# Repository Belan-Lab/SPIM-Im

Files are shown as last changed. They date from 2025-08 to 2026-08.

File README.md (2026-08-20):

Stand With Ukraine (https://stand-with-ukraine.pp.ua)

Selective Plane Illumination Microscopy Setup
==================================

_Fluorescence Imaging Laboratory, Kyiv, Ukraine_

<p align="center">
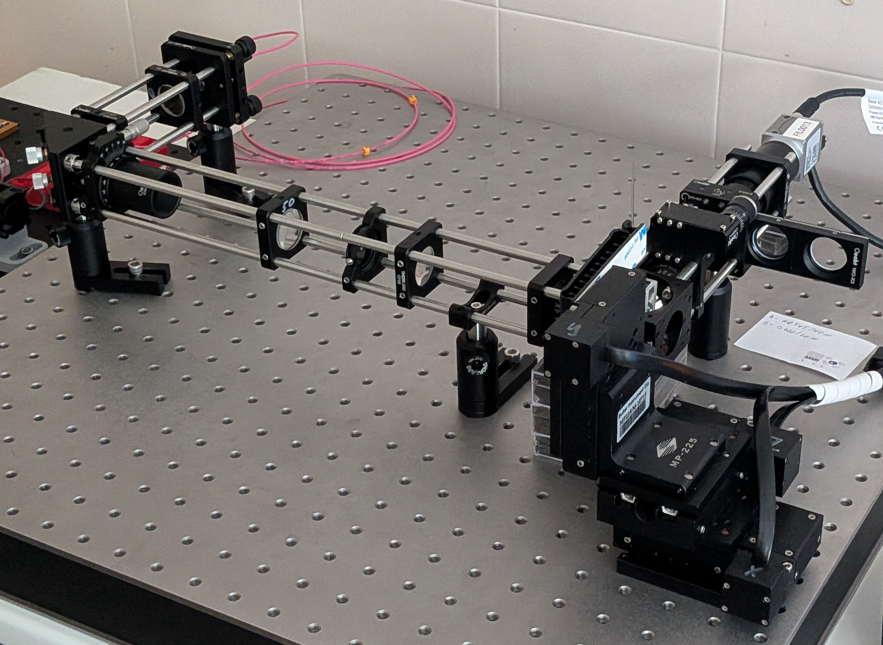
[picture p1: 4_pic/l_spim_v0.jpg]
</a>
</p>
__L-SPIM v0__

# L-SPIM v0 parameters overview

| Parameter                                      | Value                                                        |
| ---------------------------------------------- | ------------------------------------------------------------ |
| Detection objective                            | Olympus PlaN 10x 0.25                                        |
| Magnification                                  | 5.56x                                                        |
| Camera                                         | Basler Ace 2R Pro (a2A5320-23umPRO), 5320x3032 px (16.1 Mpx) |
| Pixel size                                     | 0.493 μm/px                                                  |
| Field of view                                  | 2.62x1.49 mm                                                 |
| Z-stack step resolution                        | 16 μstep/μm (0.0625 μm/μstep)                                |
| Lateral resolution, FWHM theoretical/estimated | 1.12 μm/2.06 μm                                              |
| Axial resolution, FWHM theoretical/estimated   | 11.70 μm/ 6.32 μm                                            |
| Excitation lasers                              | 510 nm, 640 nm                                               |
| Emission filters                               | Chroma HQ545/40m, Chroma D620/20m                            |

# Detection arm

## Detection params
| Parameter                                              | Value                               |
| ------------------------------------------------------ | ----------------------------------- |
| Detection objective                                    | Olympus PlaN 10x 0.25 FN 22 (F18)   |
| Detection tube lens                                    | F100                                |
| Magnification                                          | ~5.56x                              |
| Camera                                                 | Basler Ace 2R Pro (a2A5320-23umPRO) |
| Pixel size                                             | 0.493 μm/px                         |
| Field of view                                          | 2.62x1.49 mm                        |
| Theoretical resolution (500 nm)                        | 1.220 μm                            |
| Theoretical depth of field (500 nm, n=1.33)            | 10.640 μm                           |
| Z-stack step (Sutter Instruments MPC-200 with MP225/M) | 0.0625 μm/μstep (16 μstep/μm)       |

## Filters

# Excitation arm
## Light path

## Lasers

# Control software
## Micromanager configuration

## Camera
| Model           | Basler Ace 2R        |
| --------------- | -------------------- |
| ID              | a2A5320-23umPRO      |
| Sensor          | Sony IMX542 (CMOS)   |
| Sensor size     | 14.58x8.31 mm (1.1") |
| Sensor diagonal | 16.78 mm             |
| Pixels (HxV)    | 5320x3032 (16.1 Mpx) |
| Pixel size      | 2.74x2.74 μm         |
| Frame rate      | up to 24 fps         |

### GPIO pinout

|Pin|Function|I/O Line|Colour|
|-|-|-|-|
|1|12–24 VDC camera power|-|Brown|
|2|Opto-coupled I/O input line|Line 1|White|
|3|Ground for opto-coupled I/O line|-|Blue|
|4|General purpose I/O (GPIO) line|__Line 2__|Black|
|5|General purpose I/O (GPIO) line|Line 3|Grey|
|6|Ground for camera power and General Purpose I/O (GPIO) lines|-|Pink|

[Basler Power-I/O Cable](https://docs.baslerweb.com/basler-power-io-cable-m8-6p-open-p)

### GPIO configuration
Pylon Viewer v7.2 camera parameters, category __Digital I/O Control__:

- __Line Selector:__ Line 2
- __Line Inverter:__ not selected
- __Line Mode:__ Output
- __Line Source:__ Acquisition Active

<p align="center">
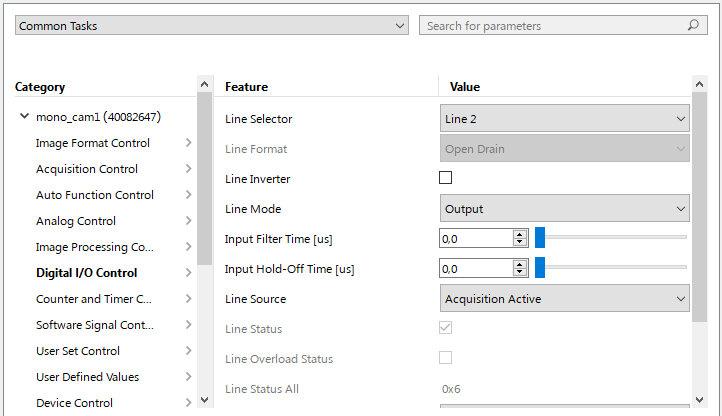
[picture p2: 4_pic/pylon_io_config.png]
</a>
</p>

## Sync

Synchronisation with [Arduino32bitBoards](https://micro-manager.org/Arduino32bitBoards), specs for ESP32:

- Baudrate: 115200
- Laser TTL trigger module requires 5V, need level conversion 3.3V -> 5V

__Pinout:__
- Trigger: __Pin 5 - camera Line 2 input__
- Channel 1: __Pin 25/DAC - Level Converter ON__
- Channel 2: __Pin 26/DAC - 510 nm trigger__
- Channel 3: __Pin 27/PWM - 640 nm trigger__
- Channel 4: Pin 15/PWM
- Channel 5: Pin 14/PWM
- Channel 6: Pin 4/PWM
- Channel 7: Pin 23/PWM
- Channel 8: Pin 19/PWM

__Switch states__
|Laser|Pin Hight|State|
|-|-|-|
|510 nm|25+26 (Ch.1+Ch.2)|3|
|640 nm|25+27 (Ch.1+Ch.3)|4 (not working)|
|510 nm + 640 nm|25+26+27 (Ch.1+Ch.2+Ch.3)|6 (not working)|

## Hardware config

# License 
This open-source project is released under the CERN Open Hardware License. Our aims are to promote open scientific hardware development and to share our engineering solutions.

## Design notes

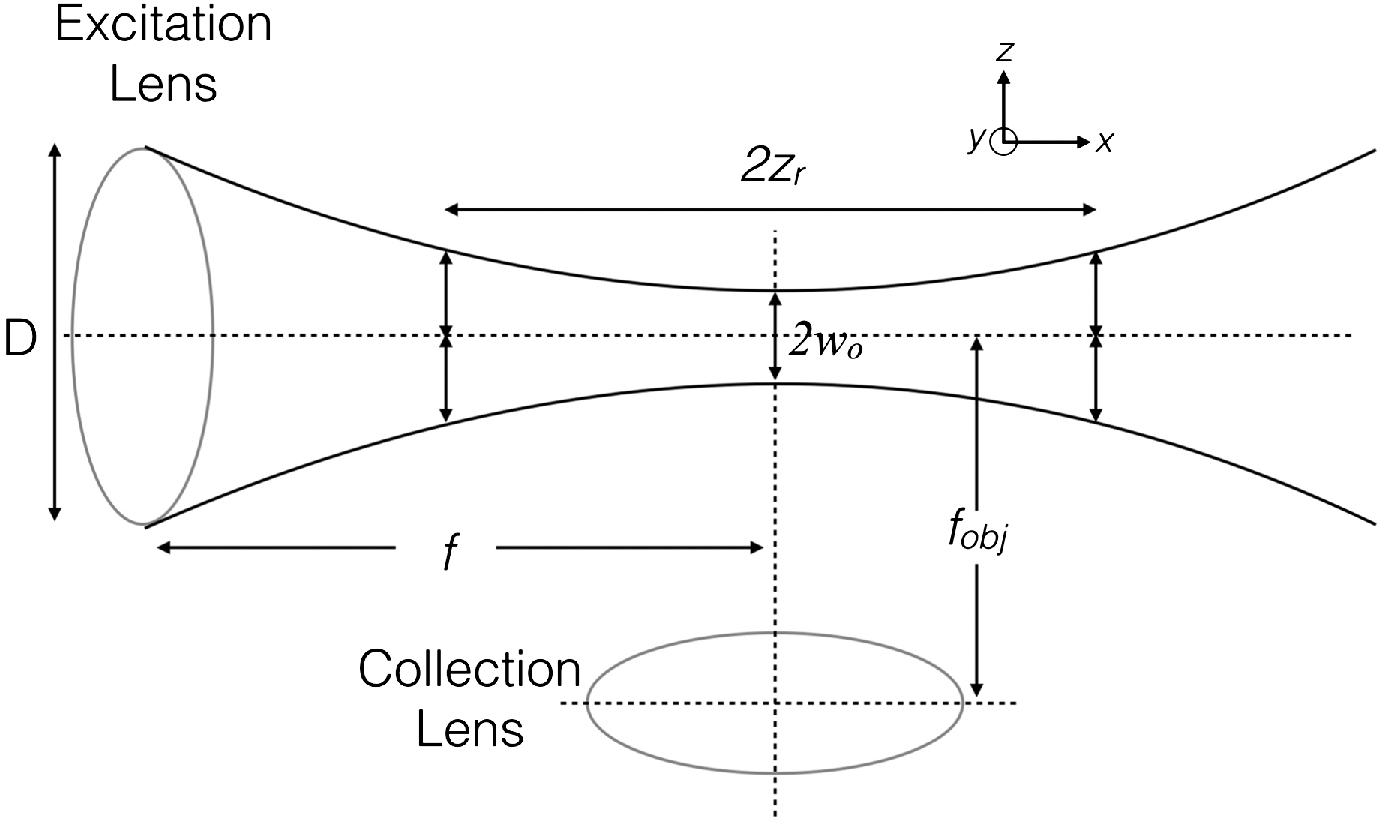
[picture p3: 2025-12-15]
3_notes/pic/ls_geom_olarte2017.jpeg

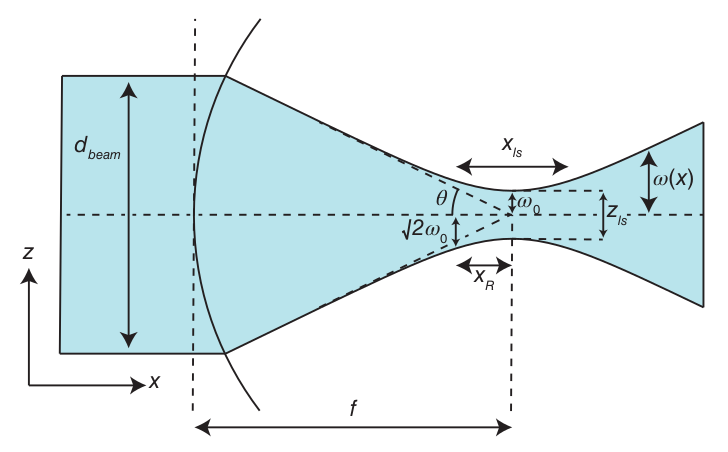
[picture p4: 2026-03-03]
3_notes/pic/gaussian_beam.png

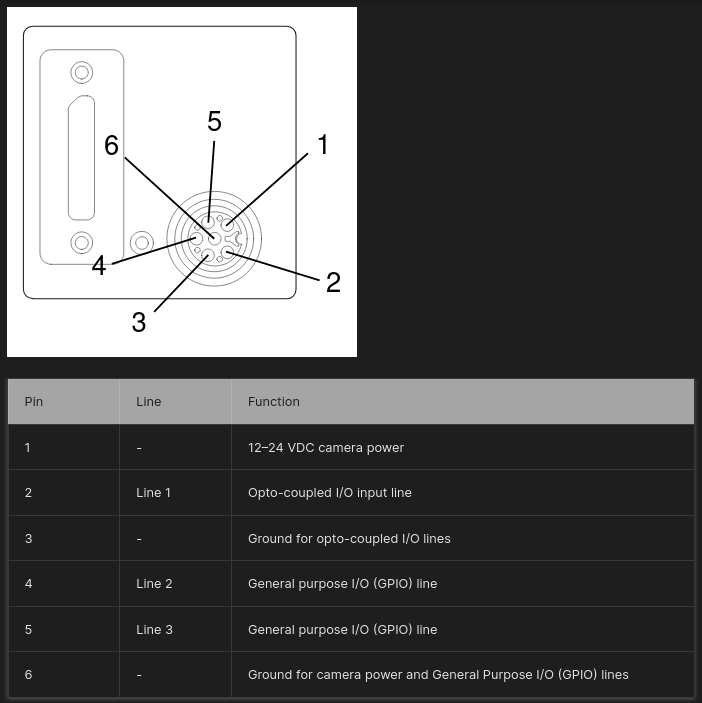
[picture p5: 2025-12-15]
3_notes/pic/GPIO_Ace2R.png

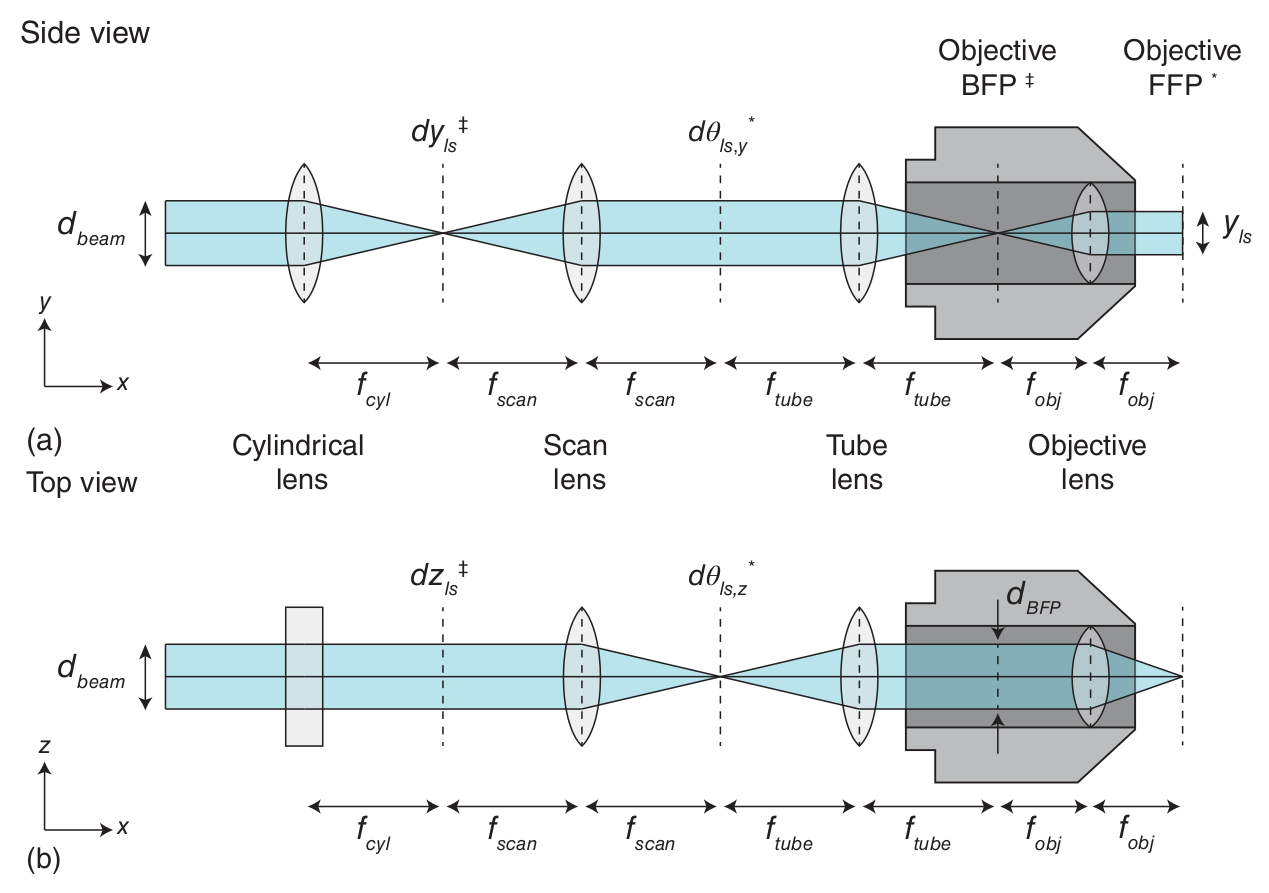
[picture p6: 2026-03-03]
3_notes/pic/illumination_path.png

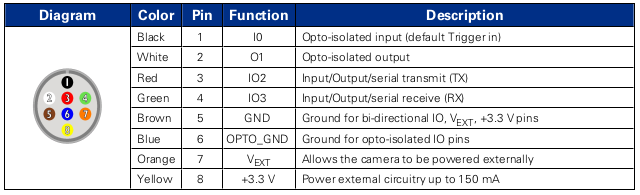
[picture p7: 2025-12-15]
3_notes/pic/GPIO_GS3.png

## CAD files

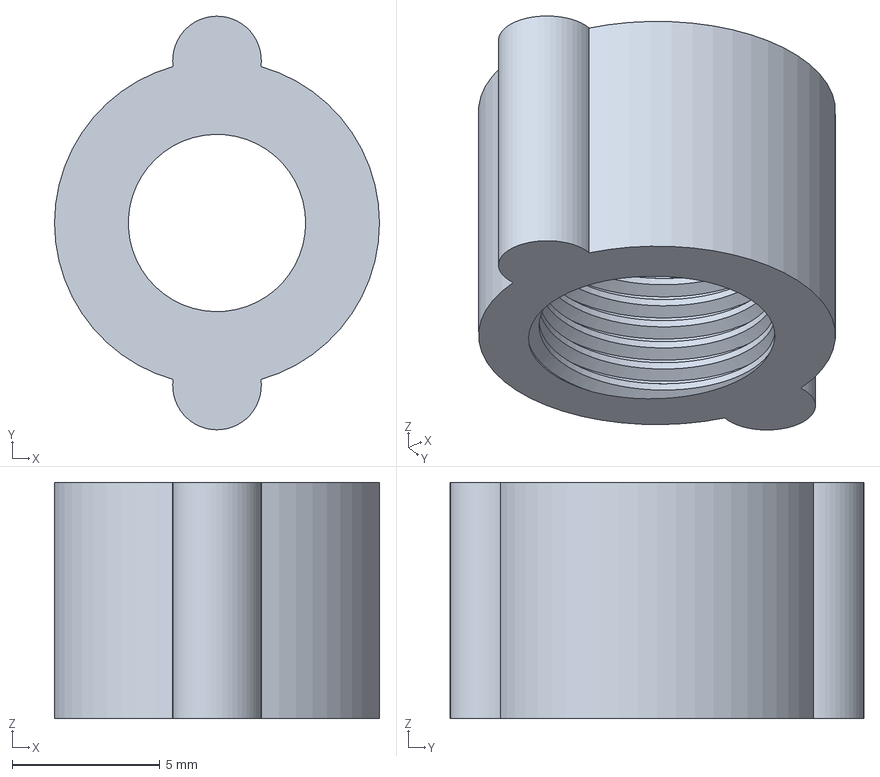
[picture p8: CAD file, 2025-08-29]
1_models/FC_colimator/FC_single_lens_colimator_v0.FCStd
11.0 x 14.0 x 8.00 mm

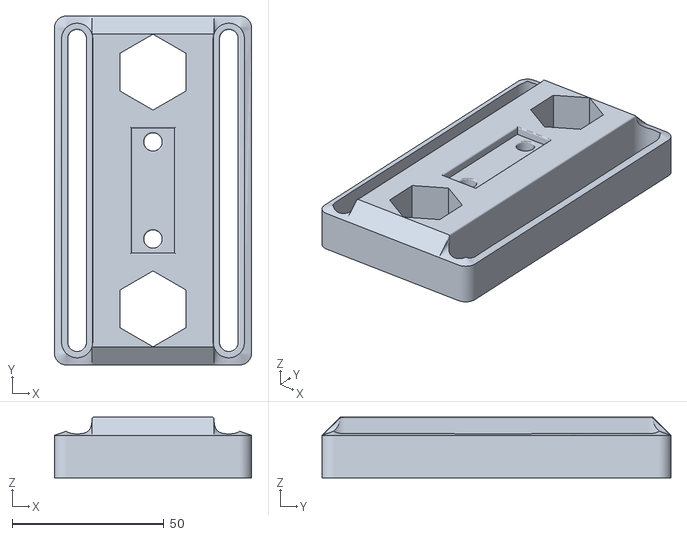
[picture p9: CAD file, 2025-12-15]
1_models/laser_combiner/0_h40mm_combiner/v2/colimator_mount_25mm_M6_platform_v0.stl
65.0 x 115.0 x 20.0

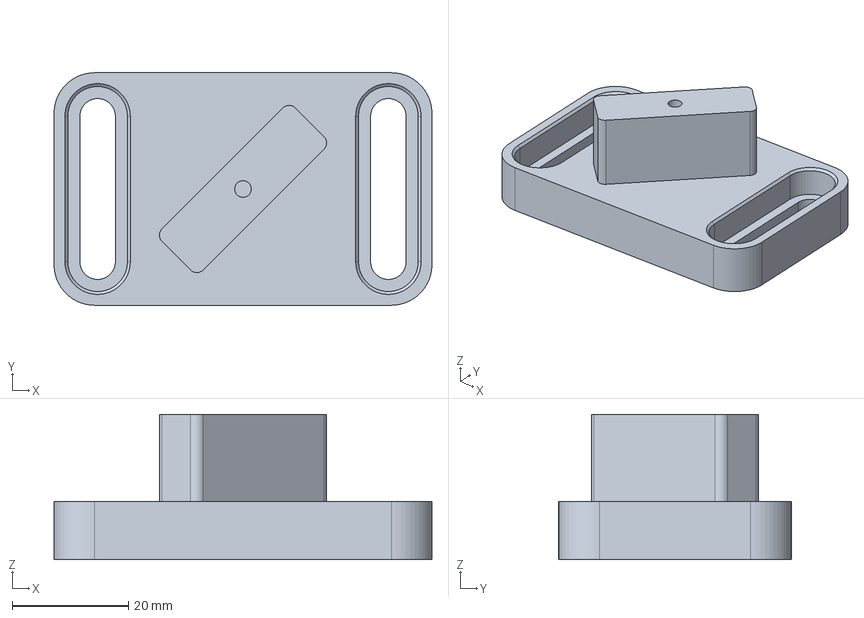
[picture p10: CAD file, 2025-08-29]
1_models/laser_combiner/kinematic_stand/25mm_M6_stand_v0.FCStd
65.0 x 40.0 x 25.0 mm

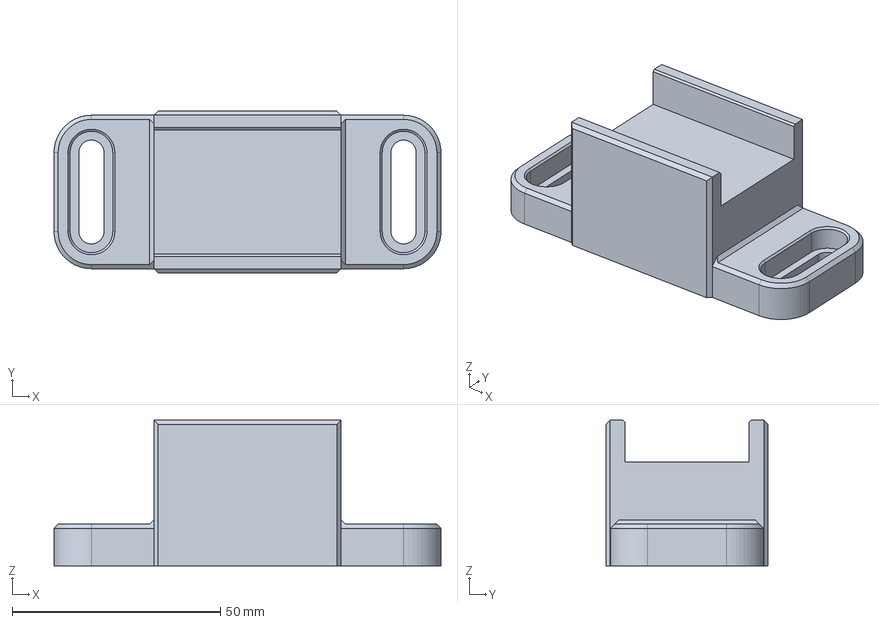
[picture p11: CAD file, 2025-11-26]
1_models/laser_combiner/laser_breadboard_mount/25mm_M6_board_v2.FCStd
93.0 x 38.9 x 35.0 mm

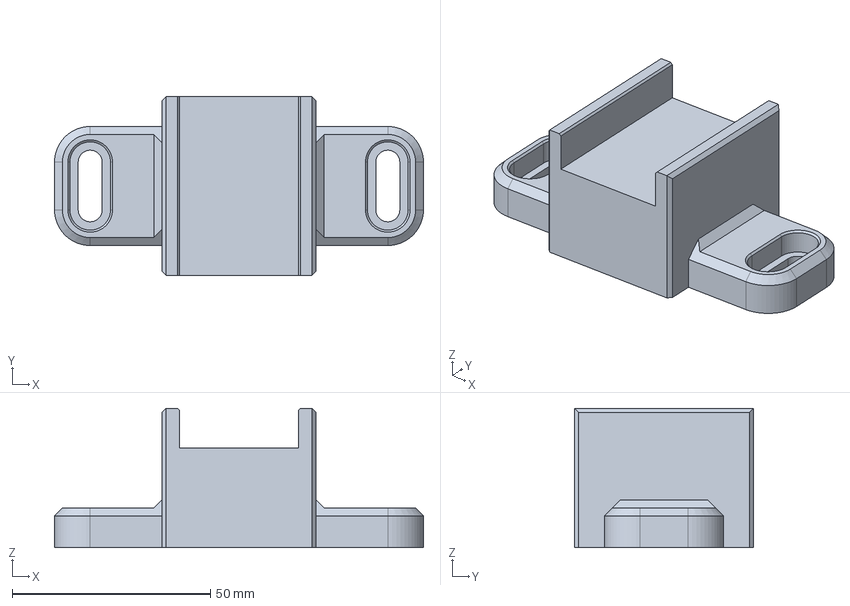
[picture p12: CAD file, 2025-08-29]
1_models/laser_combiner/laser_breadboard_mount/specific_models/laserland_505nm_100mW_25mm_M6_board_v1.FCStd
93.0 x 45.0 x 35.1 mm

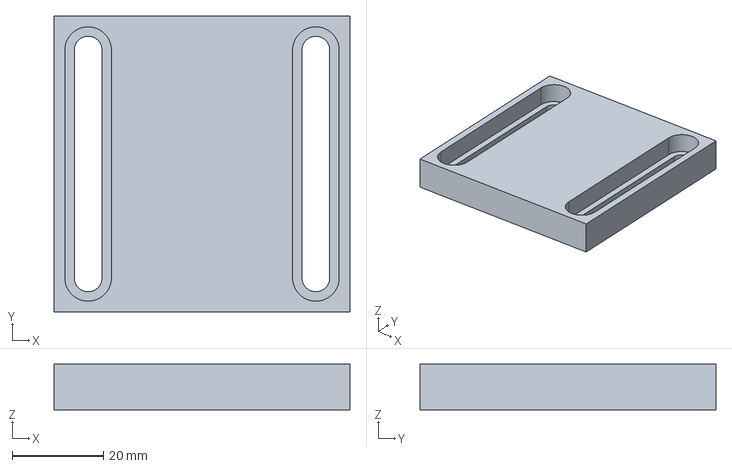
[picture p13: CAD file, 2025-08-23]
1_models/laser_combiner/laser_combiner_colimator_stand/colimator_stand.FCStd
65.0 x 65.0 x 10.0 mm

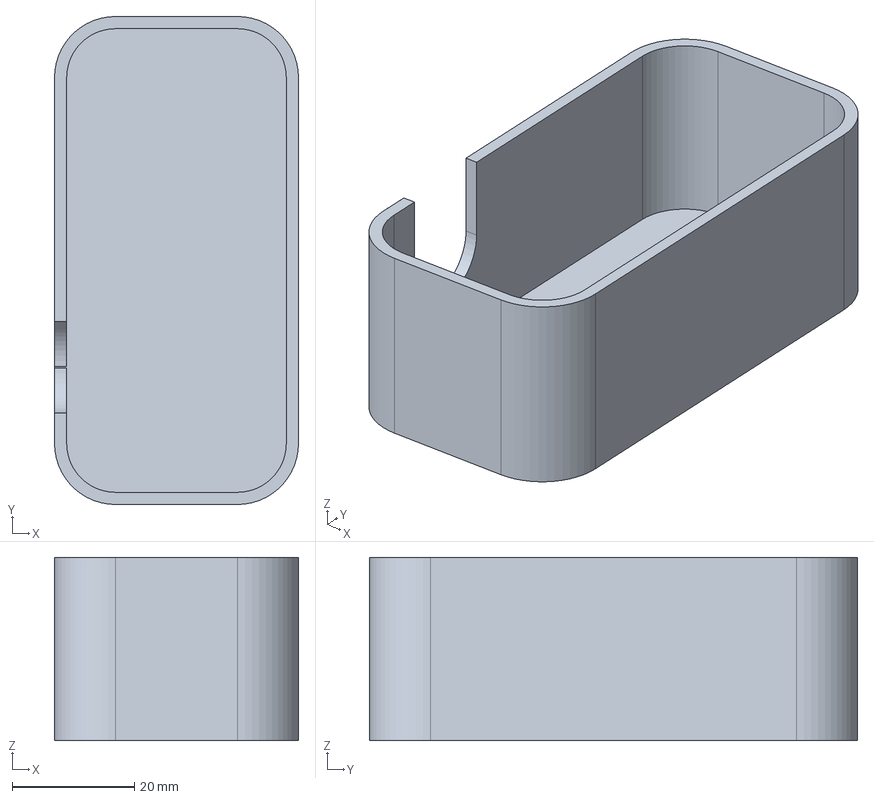
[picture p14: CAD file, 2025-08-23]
1_models/laser_combiner/laser_combiner_cover/laser_combiner_cover_v0.FCStd
40.0 x 80.0 x 30.0 mm

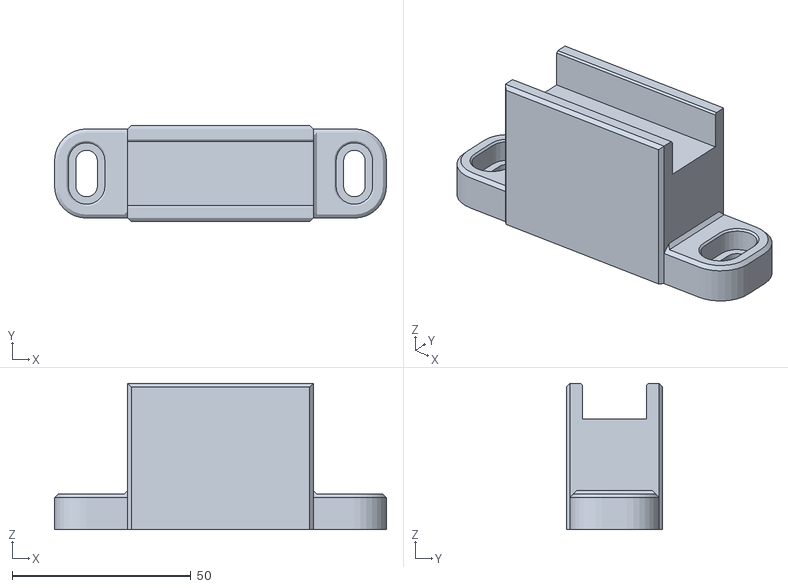
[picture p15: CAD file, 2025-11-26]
1_models/laser_combiner/0_h40mm_combiner/v2/laserland_620_100mW_h40_25mm_M6_board_v2.stl
93.0 x 27.0 x 41.0

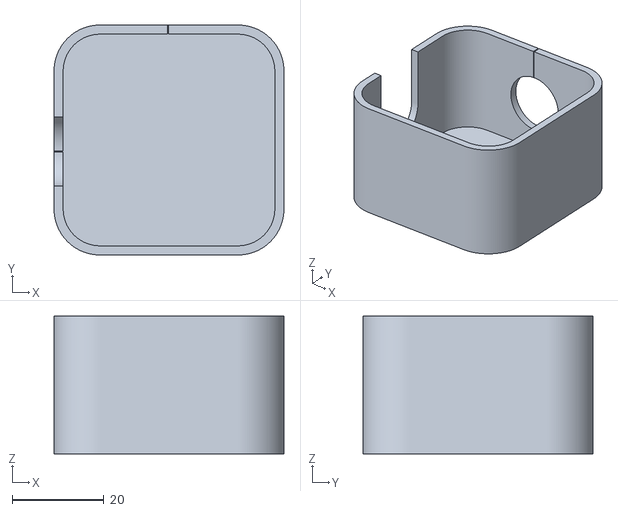
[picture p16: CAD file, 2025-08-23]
1_models/laser_combiner/laser_combiner_cover/laser_combiner_cover_v1-Body.stl
50.0 x 50.0 x 30.0

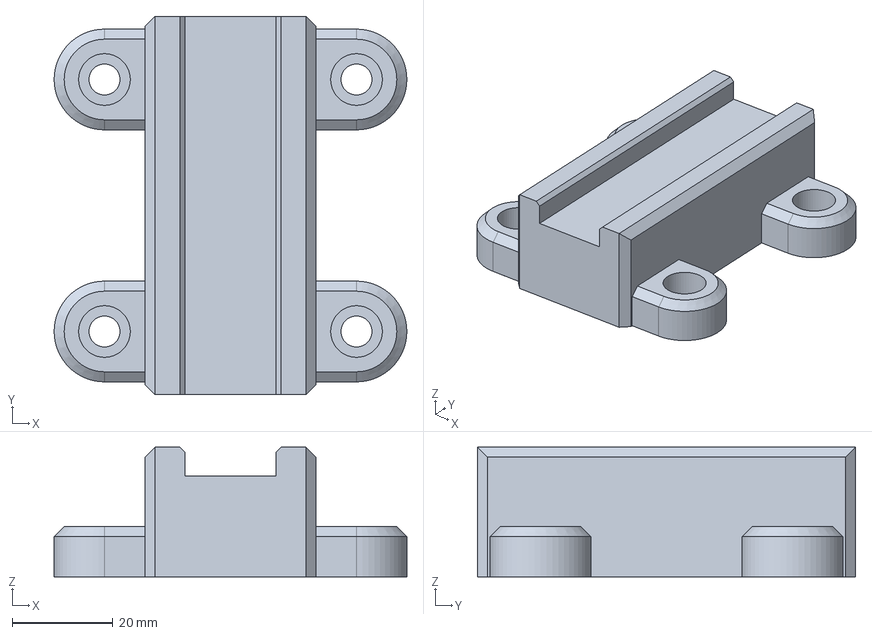
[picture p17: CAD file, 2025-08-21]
1_models/laser_combiner/laser_breadboard_mount/25mm_M6_board_v0.FCStd
70.0 x 75.0 x 25.8 mm

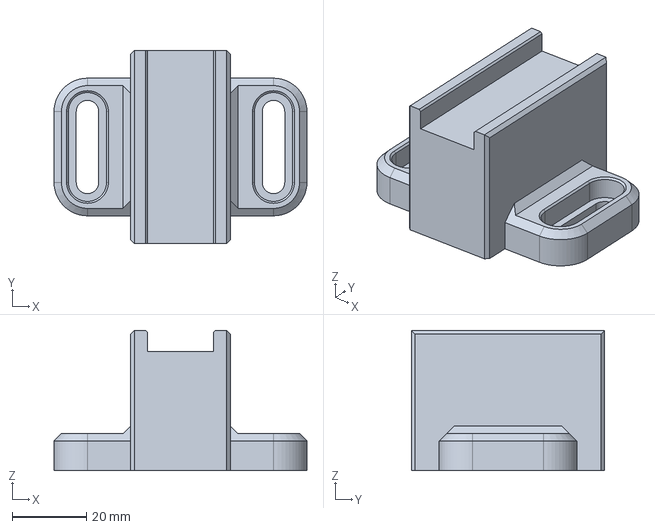
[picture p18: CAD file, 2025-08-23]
1_models/laser_combiner/laser_breadboard_mount/specific_models/laserland_640nm_100mW_25mm_M6_board_v1.FCStd
68.0 x 52.0 x 37.8 mm

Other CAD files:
1_models/laser_combiner/breadboard_platform/25mm_M6_platform_v0.FCStd
1_models/laser_combiner/laser_breadboard_mount/specific_models/laserland_510nm_50mW_25mm_M6_board_v1.FCStd
1_models/laser_combiner/0_h40mm_combiner/v2/laserland_510_50mW_h40_25mm_M6_board_v2.stl
1_models/laser_combiner/laser_combiner_cover/laser_combiner_cover_v1.FCStd
1_models/laser_combiner/laser_combiner_cover/laser_combiner_cover_v0-Body.stl
1_models/laser_combiner/0_h40mm_combiner/v1/laser_505nm_25mm_M6_board_v1-h40.stl
1_models/FC_colimator/FC_single_lens_colimator_v0.stl
1_models/laser_combiner/0_h40mm_combiner/v1/dichro_25mm_M6_stand_v0-h40mm.stl
1_models/laser_combiner/0_h40mm_combiner/v1/dichro_25mm_M6_stand_v1-h40mm.stl
1_models/laser_combiner/0_h40mm_combiner/v1/laser_510nm_25mm_M6_board_v1-h40mm.stl
1_models/laser_combiner/0_h40mm_combiner/v1/laser_640nm_25mm_M6_board_v1-h40mm.stl

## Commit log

2025-08-21 21.08.2025: laser stand
    [25mm_M6_board-640nm_mount_v0.stl, 25mm_M6_board_v0.FCStd, 25mm_M6_board_v1-640nm_mount.stl, 25mm_M6_board_v1.FCStd]
2025-08-23 23.09.2025: add cover for laser combiner
    [25mm_M6_board_v1.FCStd, 25mm_M6_platform_v0.FCStd, 25mm_M6_stand_v0.FCStd, dichro_25mm_M6_stand_v0-h40mm.stl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]
2026-05-14 14.05.2026: ctrl commit
    [50ml_slider_v0-test.stl, 50ml_slider_v0.FCStd, 50ml_slider_v1-test.stl, 50ml_slider_v1.FCStd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]
